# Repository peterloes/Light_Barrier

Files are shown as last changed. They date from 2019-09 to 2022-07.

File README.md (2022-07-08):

# Light barriers

A standalone platform for animal observation and manipulation.

This program is a software module for the hardware platform
"Light_Barrier_2015_3" developed for two pairs of lightbarriers.

Wide Input Voltage Range: 3.3V to 60V

Example with receiver from Vishay: TSSP58038 and LED Vishay: VSLB3940

Always low level triggered for wire monitoring(breakage).

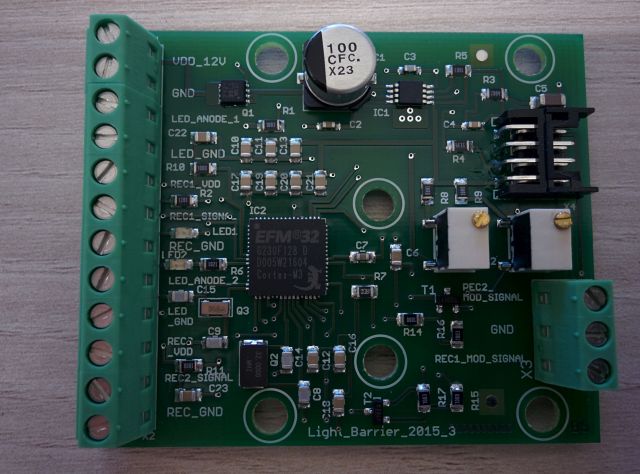
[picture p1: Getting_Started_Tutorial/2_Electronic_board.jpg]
My image


Two high level signal: 204µA@3,3V  -- Two low  level signal: 1.49mA@3,3V

Two high level signal: 195µA@5V    -- Two low  level signal: 1.49mA@5V

Two high level signal: 195µA@13,2V -- Two low  level signal: 1.47mA@13,2V

Parameter distance 3,3 Meter: 4mA@12V average

My image

Prototype: Bat counter 

The distance from light barrier 1 is 15cm and from light barrier 2 is 13cm.

https://github.com/peterloes/Light_Barrier/blob/master/Getting_Started_Tutorial/1_poster_overview_LightBarrier_Counter.pdf

Prototype: Long range RFID- reader for shore birds

https://github.com/peterloes/Light_Barrier/blob/master/Getting_Started_Tutorial/1_poster_overview_MOMO_LB_LR.pdf

Mainboard:

https://github.com/peterloes/MOMO

https://github.com/peterloes/RFID-MS

Manufacture:

https://github.com/peterloes/Light_Barrier/blob/master/Getting_Started_Tutorial/3_Supplier.txt

EXTENSION:

https://github.com/peterloes/SmartAnimalTraps

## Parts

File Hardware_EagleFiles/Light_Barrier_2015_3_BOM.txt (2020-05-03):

Partlist exported at 8/3/2016 8:29:31 AM

Part  Value                Device                  Package                Description                                                    
C1    100uF/16V            CPOL-EUE                PANASONIC_E            POLARIZED CAPACITOR, European symbol                           
C2    1uF                  C-EUC0603               C0603                  CAPACITOR, European symbol                                     
C3    1nF                  C-EUC0603               C0603                  CAPACITOR, European symbol                                     
C4    10nF                 C-EUC0603               C0603                  CAPACITOR, European symbol                                     
C5    10uF                 C-EUC1206               C1206                  CAPACITOR, European symbol                                     
C6    100n                 C_SMD0805               0805                                                                                  
C7    1u                   C_SMD0805               0805                                                                                  
C8    12p                  C_SMD0805               0805                                                                                  
C9    18p                  C_SMD0805               0805                                                                                  
C10   100n                 C_SMD0805               0805                                                                                  
C11   100n                 C_SMD0805               0805                                                                                  
C12   100n                 C_SMD0805               0805                                                                                  
C13   100n                 C_SMD0805               0805                                                                                  
C14   12p                  C_SMD0805               0805                                                                                  
C15   18p                  C_SMD0805               0805                                                                                  
C16   100n                 C_SMD0805               0805                                                                                  
C17   100n                 C_SMD0805               0805                                                                                  
C18   100n                 C_SMD0805               0805                                                                                  
C19   100n                 C_SMD0805               0805                                                                                  
C20   100n                 C_SMD0805               0805                                                                                  
C21   100n                 C_SMD0805               0805                                                                                  
C22   100n                 C-EUC0805               C0805                  CAPACITOR, European symbol                                     
C23   100n                 C-EUC0805               C0805                  CAPACITOR, European symbol                                     
IC1   TPS7A1601DGNT        TPS7A16                 DGN_S-PDSO-G8-EXP                                                                     
IC2   EFM32G230F128        EFM32G230F128           QFN64                  EFM32G230F128 Gecko Microcontroller in 9mm x 9mm QFN64 package 
LED1  SML-211UT            LEDCHIPLED_0805         CHIPLED_0805           LED                                                            
LED2  SML-211UT            LEDCHIPLED_0805         CHIPLED_0805           LED                                                            
PASS1 ROUND_1MM1.5         ROUND_1MM1.5            ROUND2_1.5MM                                                                          
PASS2 ROUND_1MM1.5         ROUND_1MM1.5            ROUND2_1.5MM                                                                          
Q1    SI7121DN             TRANSISTOR-FET_SI7113DN TRANSISTOR-FET_1212-8S                                                                
Q2    NX5032GA/32MHz/8pF   CRYSTAL2P5.0X3.2        CRYSTAL2P5.0X3.2       Quarz Crystal                                                  
Q3    CM7V, 32768Hz/12.5pF CRYSTAL2P               CRYSTAL2P3.2X1.5       Quarz Crystal                                                  
R1    100k                 R-EU_R0805              R0805                  RESISTOR, European symbol                                      
R2    1K2                  R-EU_R0805              R0805                  RESISTOR, European symbol                                      
R3    2M                   R-EU_R0805              R0805                  RESISTOR, European symbol                                      
R4    1M13                 R-EU_R0805              R0805                  RESISTOR, European symbol                                      
R5    100K                 R-EU_R0805              R0805                  RESISTOR, European symbol                                      
R6    1K2                  R-EU_R0805              R0805                  RESISTOR, European symbol                                      
R7    1                    R-EU_R0805              R0805                  RESISTOR, European symbol                                      
R8    18                   R-EU_R0805              R0805                  RESISTOR, European symbol                                      
R9    18                   R-EU_R0805              R0805                  RESISTOR, European symbol                                      
R10   100                  R-EU_R0805              R0805                  RESISTOR, European symbol                                      
R11   100                  R-EU_R0805              R0805                  RESISTOR, European symbol                                      
R12   50k(TS63)            R-TRIMMTS63Y            RTRIMTS63Y             Trimm resistor                                                 
R13   50k(TS63)            R-TRIMMTS63Y            RTRIMTS63Y             Trimm resistor                                                 
R14   100                  R-EU_R0805              R0805                  RESISTOR, European symbol                                      
R15   100                  R-EU_R0805              R0805                  RESISTOR, European symbol                                      
R16   100K                 R-EU_R0805              R0805                  RESISTOR, European symbol                                      
R17   100K                 R-EU_R0805              R0805                  RESISTOR, European symbol                                      
T1    2N7002               ZETEX_NMOSSOT23         ZETEX_SOT-23           MOS FET                                                        
T2    2N7002               ZETEX_NMOSSOT23         ZETEX_SOT-23           MOS FET                                                        
X1    MKDS1/2-3,81         MKDS1/2-3,81            2POL381                MKDS 1/2-3,81 - Order No. 1727010 (RS-Online - 101-5384)       
X2    MKDS1/10-3,81        MKDS1/10-3,81           10POL381               MKDS 1/10-3,81 - Order No. 1727094                             
X3    MKDS1/3-3,81         MKDS1/3-3,81            3POL381                MKDS 1/3-3,81 - Order No. 1727023 (RS-Online - 101-5390)       
X4    DF11_8DP_2DS         DP11_8DP_2DS            DP11_8DP-2DS

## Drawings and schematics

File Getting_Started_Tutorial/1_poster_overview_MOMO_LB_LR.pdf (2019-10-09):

## Multifunctional Mainboard to Observe and Manipulate Organisms (MOMO) Light Barrier and Long Range Reader

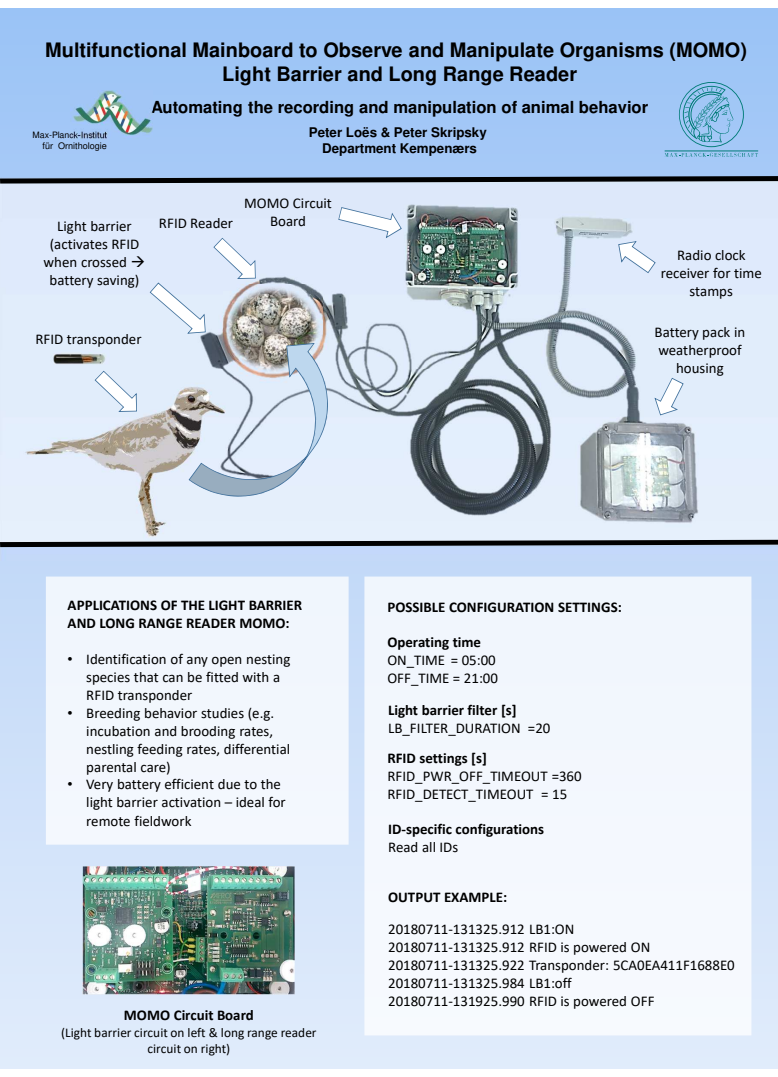
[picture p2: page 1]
APPLICATIONS OF THE LIGHT BARRIER; POSSIBLE CONFIGURATION SETTINGS:; RFID Reader; RFID transponder; Operating time ON_TIME = 05:00 OFF_TIME = 21:00; MOMO Circuit Board; Light barrier (activates RFID when crossed → battery saving); RFID settings [s] RFID_PWR_OFF_TIMEOUT =360 RFID_DETECT_TIMEOUT = 15; OUTPUT EXAMPLE:

Automating the recording and manipulation of animal behavior

Peter Loës & Peter Skripsky
Department Kempenærs

Max-Planck-Institut
für Ornithologie

Radio clock
receiver for time
stamps

Battery pack in
weatherproof
housing

AND LONG RANGE READER MOMO:

• Identification of any open nesting
species that can be fitted with a
RFID transponder
• Breeding behavior studies (e.g.
incubation and brooding rates,
nestling feeding rates, differential
parental care)
• Very battery efficient due to the
light barrier activation – ideal for
remote fieldwork

Light barrier filter [s]
LB_FILTER_DURATION =20

ID-specific configurations
Read all IDs

20180711-131325.912 RFID is powered ON
20180711-131325.922 Transponder: 5CA0EA411F1688E0
20180711-131325.984 LB1:off
20180711-131925.990 RFID is powered OFF

MOMO Circuit Board

(Light barrier circuit on left & long range reader

circuit on right)

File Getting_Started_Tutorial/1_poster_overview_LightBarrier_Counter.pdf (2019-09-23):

### Light Barrier Counter

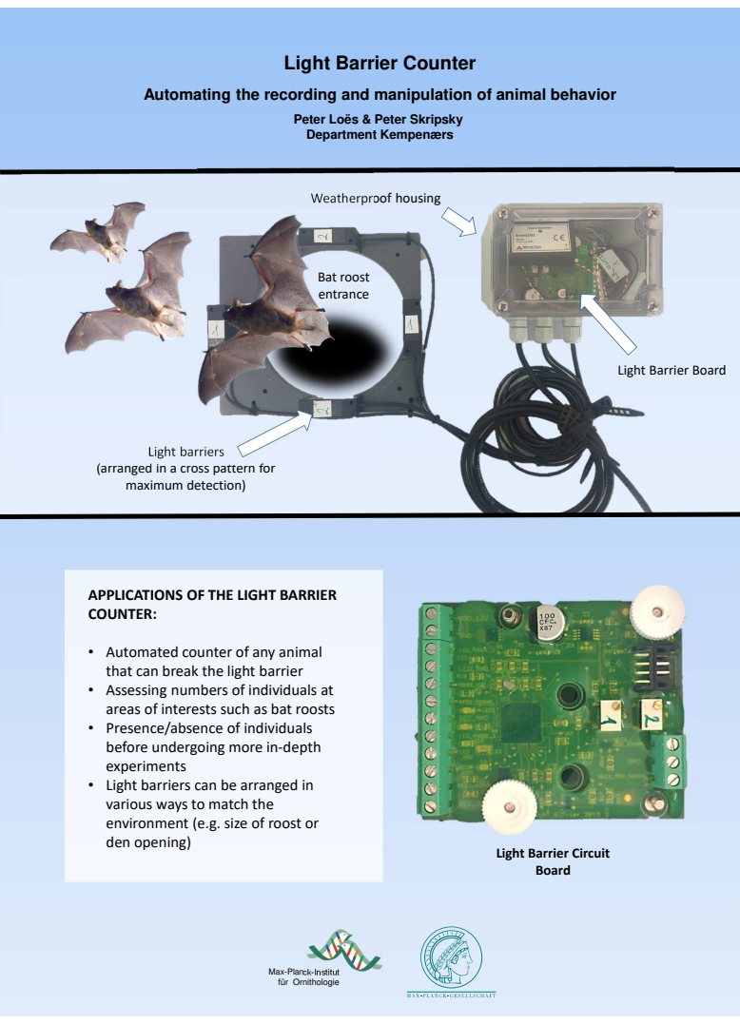
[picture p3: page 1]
Board; Weatherproof housing; Light barriers; Bat roost entrance

Automating the recording and manipulation of animal behavior

Peter Loës & Peter Skripsky
Department Kempenærs

Light Barrier Board

(arranged in a cross pattern for
maximum detection)

APPLICATIONS OF THE LIGHT BARRIER
COUNTER:

• Automated counter of any animal
that can break the light barrier
• Assessing numbers of individuals at
areas of interests such as bat roosts
• Presence/absence of individuals
before undergoing more in-depth
experiments
• Light barriers can be arranged in
various ways to match the
environment (e.g. size of roost or
den opening)

Light Barrier Circuit

Max-Planck-Institut
für Ornithologie

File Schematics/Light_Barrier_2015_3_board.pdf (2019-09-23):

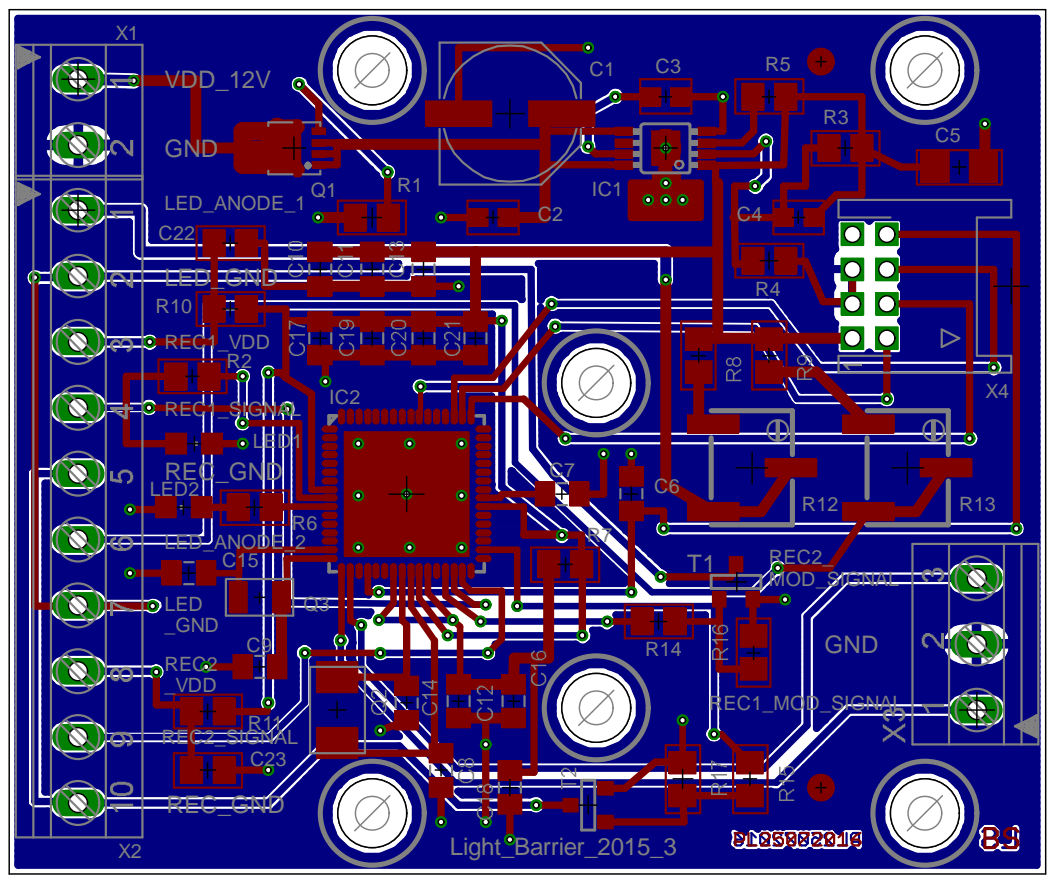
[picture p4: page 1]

GND

LED_ANODE_1
C22

LED1

R11
C23

REC2_SIGNAL

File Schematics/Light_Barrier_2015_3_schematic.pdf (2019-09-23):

# Power Input

# EFM32 Power Regulator

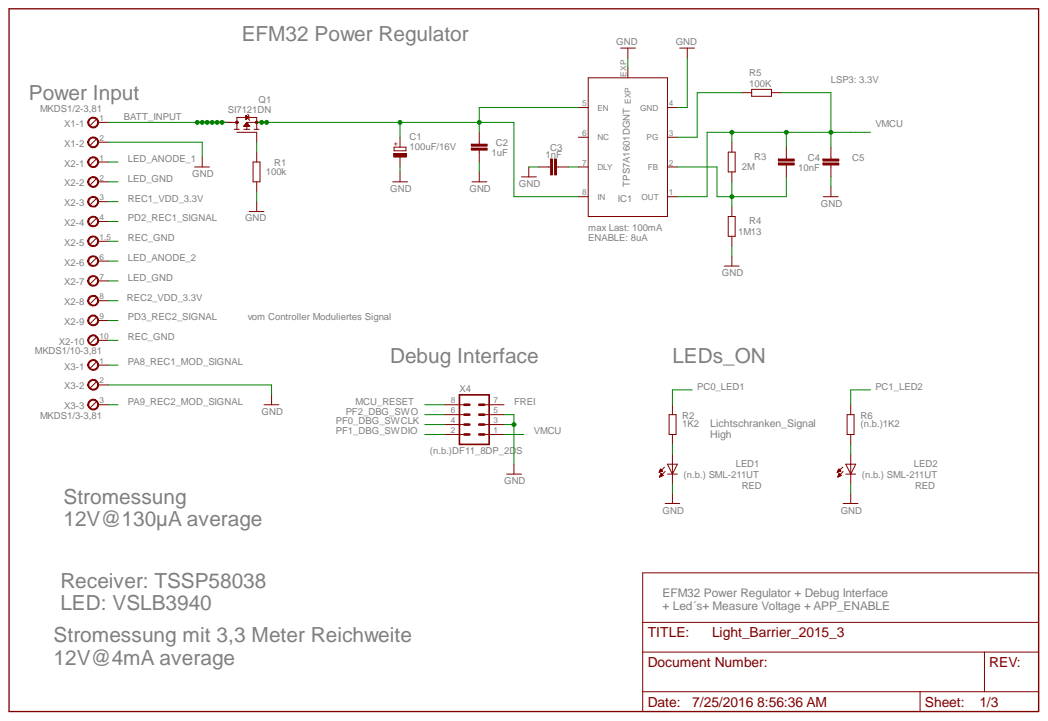
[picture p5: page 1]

vom Controller Moduliertes Signal

EFM32 Power Regulator + Debug Interface
+ Led´s+ Measure Voltage + APP_ENABLE
TITLE:

Document Number: | REV:

Date: 7/25/2016 8:56:36 AM | Sheet: 1/3

# EFM32 I/O + POWER

# CL f. 32KHz crystal = 22pF as in STK3600

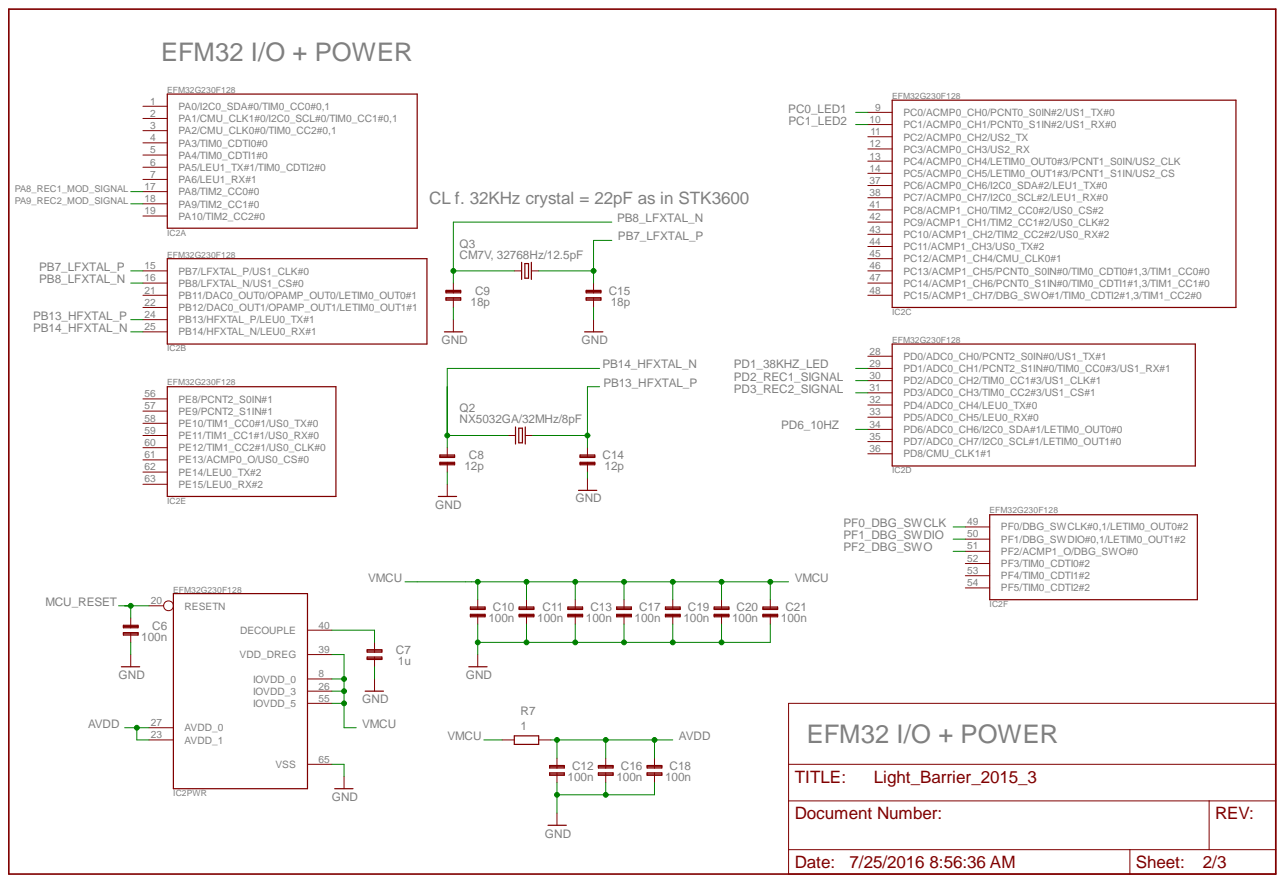
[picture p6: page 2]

Document Number: | REV:

Date: 7/25/2016 8:56:36 AM | Sheet: 2/3

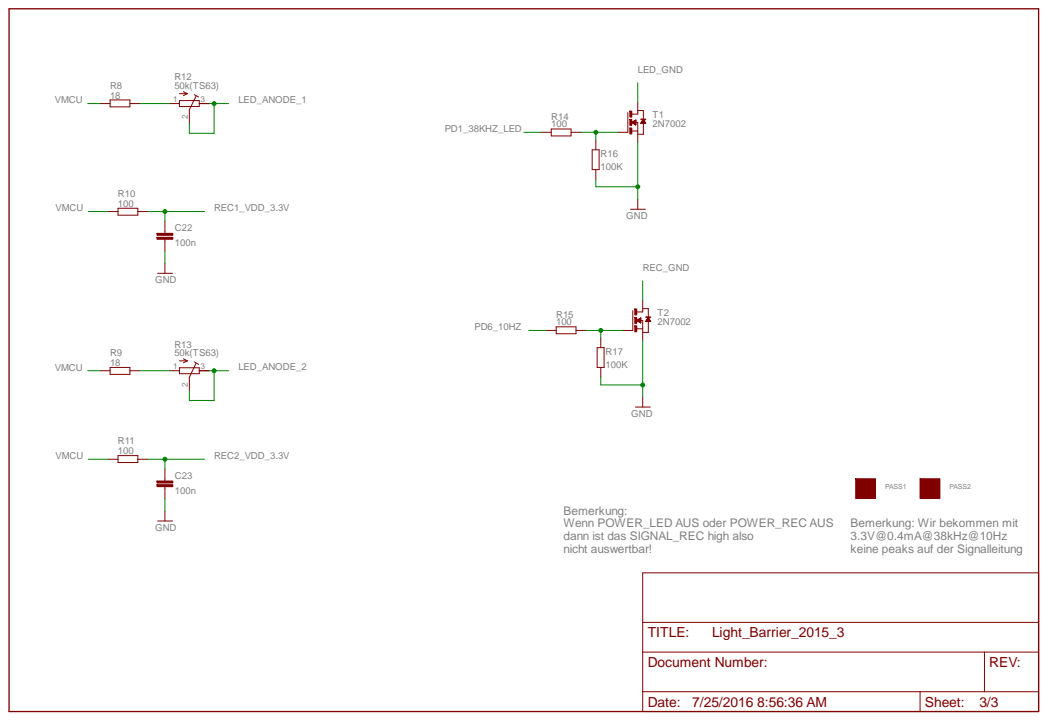
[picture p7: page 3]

Bemerkung:
Wenn POWER_LED AUS oder POWER_REC AUS
dann ist das SIGNAL_REC high also
nicht auswertbar!

Bemerkung: Wir bekommen mit
3.3V@0.4mA@38kHz@10Hz
keine peaks auf der Signalleitung

Document Number: | REV:

Date: 7/25/2016 8:56:36 AM | Sheet: 3/3

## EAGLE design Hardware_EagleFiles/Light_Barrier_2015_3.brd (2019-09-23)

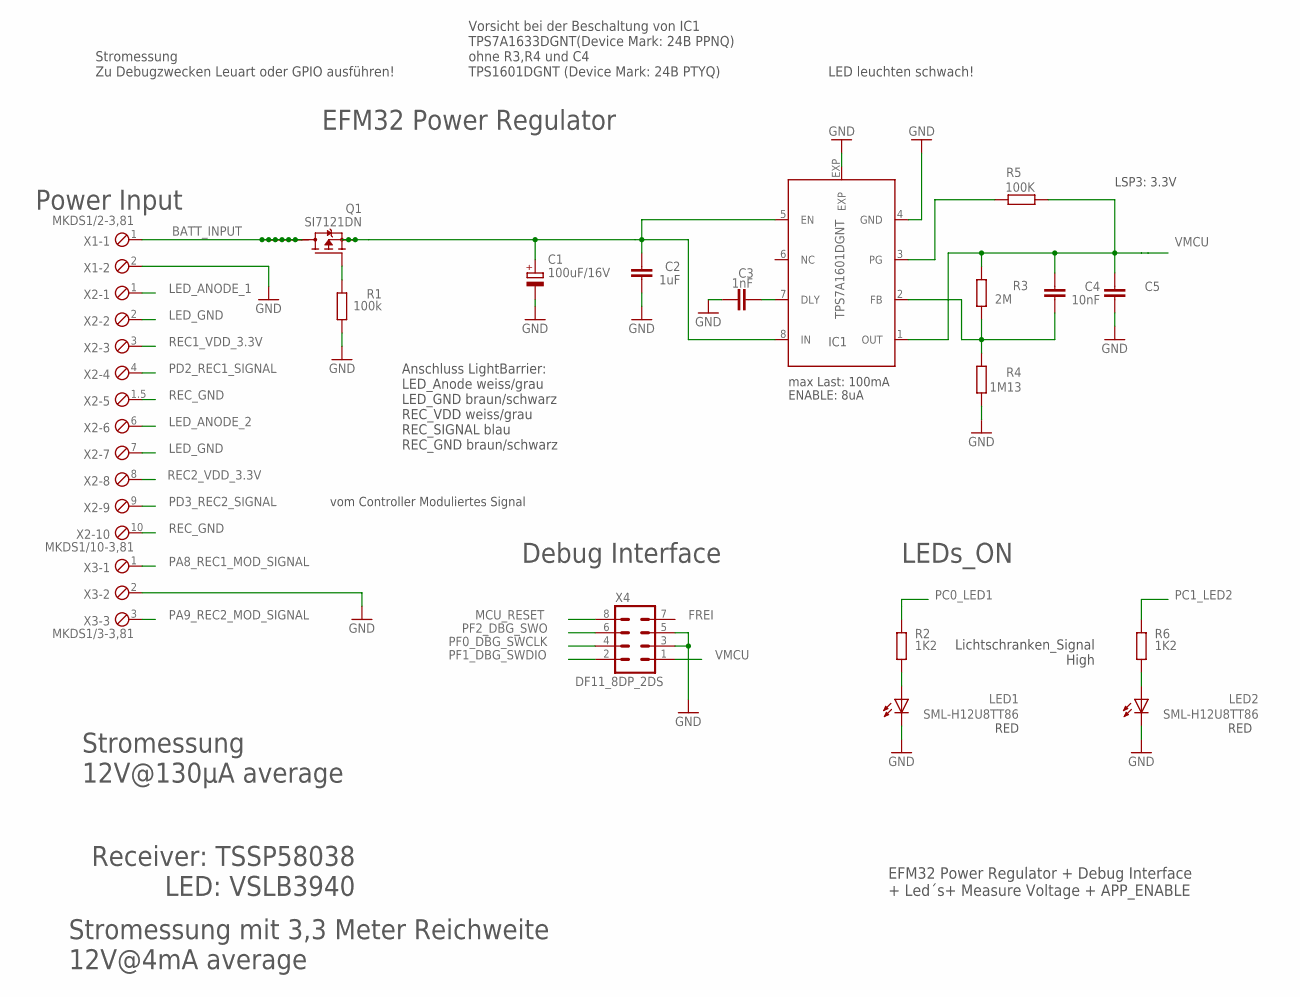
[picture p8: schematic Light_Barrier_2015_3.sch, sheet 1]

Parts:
C1: 100uF/16V; PANASONIC_E
C2: 1uF; C0603
C3: 1nF; C0603
C4: 10nF; C0603
C5: 10uF; C1206
IC1: TPS7A1601DGNT; DGN_S-PDSO-G8-EXP
LED1, LED2: SML-H12U8TT86; CHIPLED_0805
Q1: SI7121DN; TRANSISTOR-FET_1212-8S
R1: 100k; R0805
R2, R6: 1K2; R0805
R3: 2M; R0805
R4: 1M13; R0805
R5: 100K; R0805
X1: MKDS1/2-3,81; 2POL381
X2: MKDS1/10-3,81; 10POL381
X3: MKDS1/3-3,81; 3POL381
X4: DF11_8DP_2DS; DP11_8DP-2DS

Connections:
BATT_INPUT: Q1.5 (D), Q1.6 (D), Q1.7 (D), Q1.8 (D), Q1.9 (D), Q1.10 (D), Q1.11 (D), X1.1
GND: C1.-, C2.1, C3.1, C5.1, IC1.4 (GND), IC1.EXP, LED1.C, LED2.C, R1.1, R4.1, X1.2, X3.2, X4.3, X4.5; also elsewhere on the board
LED_ANODE_1: X2.1; also elsewhere on the board
LED_ANODE_2: X2.6; also elsewhere on the board
LED_GND: X2.2, X2.7; also elsewhere on the board
MCU_RESET: X4.8; also elsewhere on the board
unnamed: C4.1, IC1.2 (FB), R3.1, R4.2
unnamed: C3.2, IC1.7 (DLY)
unnamed: C1.+, C2.2, IC1.5 (EN), IC1.8 (IN), Q1.1 (S), Q1.2 (S), Q1.3 (S)
unnamed: IC1.3 (PG), R5.2
unnamed: Q1.4 (G), R1.2
unnamed: LED1.A, R2.2
unnamed: LED2.A, R6.2
PA8_REC1_MOD_SIGNAL: X3.1; also elsewhere on the board
PA9_REC2_MOD_SIGNAL: X3.3; also elsewhere on the board
PC0_LED1: R2.1; also elsewhere on the board
PC1_LED2: R6.1; also elsewhere on the board
PD2_REC1_SIGNAL: X2.4; also elsewhere on the board
PD3_REC2_SIGNAL: X2.9; also elsewhere on the board
PF0_DBG_SWCLK: X4.4; also elsewhere on the board
PF1_DBG_SWDIO: X4.2; also elsewhere on the board
PF2_DBG_SWO: X4.6; also elsewhere on the board
REC1_VDD_3.3V: X2.3; also elsewhere on the board
REC2_VDD_3.3V: X2.8; also elsewhere on the board
REC_GND: X2.1.5, X2.10; also elsewhere on the board
VMCU: C4.2, C5.2, IC1.1 (OUT), R3.2, R5.1, X4.1; also elsewhere on the board

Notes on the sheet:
EFM32 Power Regulator + Debug Interface + Led´s+ Measure Voltage + APP_ENABLE
ENABLE: 8uA
Power Input
max Last: 100mA
LSP3: 3.3V
EFM32 Power Regulator
Debug Interface
LEDs_ON
FREI
RED
Receiver: TSSP58038 LED: VSLB3940
Lichtschranken_Signal High
vom Controller Moduliertes Signal
Stromessung 12V@130µA average
Stromessung mit 3,3 Meter Reichweite 12V@4mA average
Stromessung Zu Debugzwecken Leuart oder GPIO ausführen!
Vorsicht bei der Beschaltung von IC1 TPS7A1633DGNT(Device Mark: 24B PPNQ) ohne R3,R4 und C4 TPS1601DGNT (Device Mark: 24B PTYQ)
LED leuchten schwach!
Anschluss LightBarrier: LED_Anode weiss/grau LED_GND braun/schwarz REC_VDD weiss/grau REC_SIGNAL blau REC_GND braun/schwarz

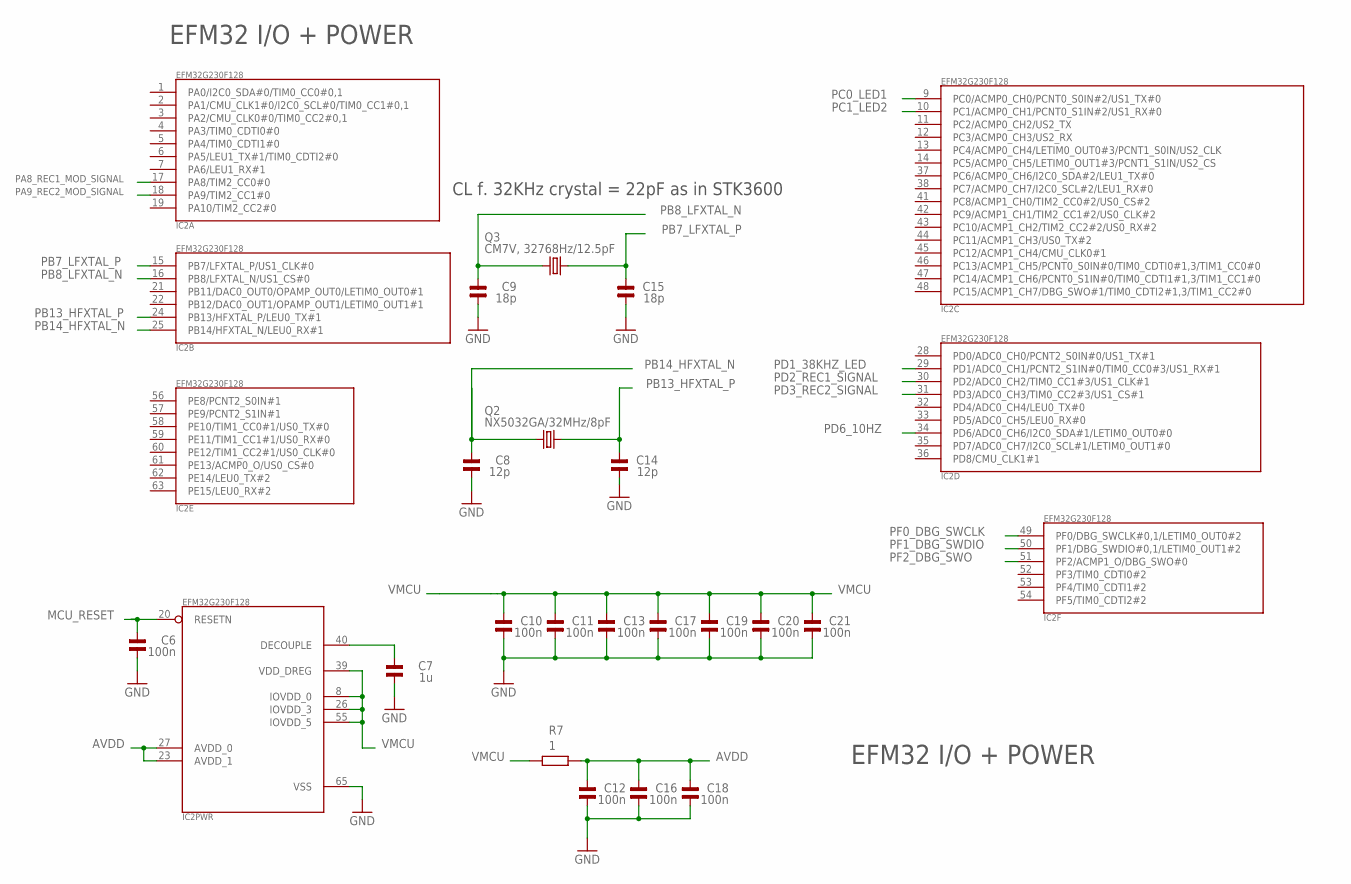
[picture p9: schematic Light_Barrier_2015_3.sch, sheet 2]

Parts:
C6, C10, C11, C12, C13, C16, C17, C18, C19, C20, C21: 100n; 0805
C7: 1u; 0805
C8, C14: 12p; 0805
C9, C15: 18p; 0805
IC2: EFM32G230F128; QFN64
Q2: NX5032GA/32MHz/8pF; CRYSTAL2P5.0X3.2
Q3: CM7V, 32768Hz/12.5pF; CRYSTAL2P3.2X1.5
R7: 1; R0805

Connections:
AVDD: C12.2, C16.2, C18.2, IC2.23 (AVDD_1), IC2.27 (AVDD_0), R7.2
GND: C6.1, C7.1, C8.1, C9.1, C10.1, C11.1, C12.1, C13.1, C14.1, C15.1, C16.1, C17.1, C18.1, C19.1, C20.1, C21.1, IC2.65 (VSS); also elsewhere on the board
MCU_RESET: C6.2, IC2.20 (RESETN); also elsewhere on the board
unnamed: C7.2, IC2.40 (DECOUPLE)
PA8_REC1_MOD_SIGNAL: IC2.17 (PA8/TIM2_CC0#0); also elsewhere on the board
PA9_REC2_MOD_SIGNAL: IC2.18 (PA9/TIM2_CC1#0); also elsewhere on the board
PB7_LFXTAL_P: C15.2, IC2.15 (PB7/LFXTAL_P/US1_CLK#0), Q3.2
PB8_LFXTAL_N: C9.2, IC2.16 (PB8/LFXTAL_N/US1_CS#0), Q3.1
PB13_HFXTAL_P: C14.2, IC2.24 (PB13/HFXTAL_P/LEU0_TX#1), Q2.2
PB14_HFXTAL_N: C8.2, IC2.25 (PB14/HFXTAL_N/LEU0_RX#1), Q2.1
PC0_LED1: IC2.9 (PC0/ACMP0_CH0/PCNT0_S0IN#2/US1_TX#0); also elsewhere on the board
PC1_LED2: IC2.10 (PC1/ACMP0_CH1/PCNT0_S1IN#2/US1_RX#0); also elsewhere on the board
PD1_38KHZ_LED: IC2.29 (PD1/ADC0_CH1/PCNT2_S1IN#0/TIM0_CC0#3/US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); also elsewhere on the board
PD2_REC1_SIGNAL: IC2.30 (PD2/ADC0_CH2/TIM0_CC1#3/US1_CLK#1); also elsewhere on the board
PD3_REC2_SIGNAL: IC2.31 (PD3/ADC0_CH3/TIM0_CC2#3/US1_CS#1); also elsewhere on the board
PD6_10HZ: IC2.34 (PD6/ADC0_CH6/I2C0_SDA#1/LETIM0_OUT0#0); also elsewhere on the board
PF0_DBG_SWCLK: IC2.49 (PF0/DBG_SWCLK#0,1/LETIM0_OUT0#2); also elsewhere on the board
PF1_DBG_SWDIO: IC2.50 (PF1/DBG_SWDIO#0,1/LETIM0_OUT1#2); also elsewhere on the board
PF2_DBG_SWO: IC2.51 (PF2/ACMP1_O/DBG_SWO#0); also elsewhere on the board
VMCU: C10.2, C11.2, C13.2, C17.2, C19.2, C20.2, C21.2, IC2.8 (IOVDD_0), IC2.26 (IOVDD_3), IC2.39 (VDD_DREG), IC2.55 (IOVDD_5), R7.1; also elsewhere on the board

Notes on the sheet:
EFM32 I/O + POWER
CL f. 32KHz crystal = 22pF as in STK3600

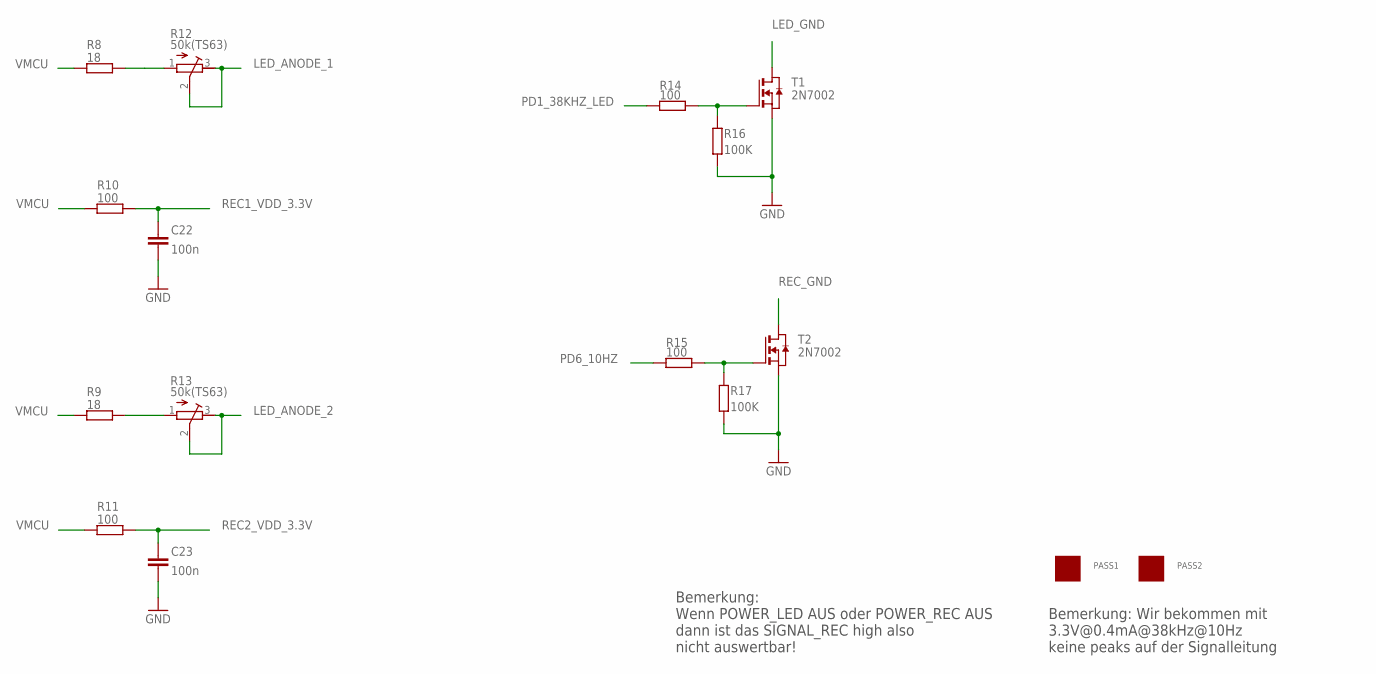
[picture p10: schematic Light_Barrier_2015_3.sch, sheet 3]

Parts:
C22, C23: 100n; C0805
PASS1, PASS2: ROUND_1MM1.5; ROUND2_1.5MM
R8, R9: 18; R0805
R10, R11, R14, R15: 100; R0805
R12, R13: 50k(TS63); RTRIMTS63Y
R16, R17: 100K; R0805
T1, T2: 2N7002; ZETEX_SOT-23

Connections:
GND: C22.2, C23.2, R16.1, R17.1, T1.2 (S), T2.2 (S); also elsewhere on the board
LED_ANODE_1: R12.2 (S), R12.3 (E); also elsewhere on the board
LED_ANODE_2: R13.2 (S), R13.3 (E); also elsewhere on the board
LED_GND: T1.1 (D); also elsewhere on the board
unnamed: R9.2, R13.1 (A)
unnamed: R8.2, R12.1 (A)
unnamed: R14.1, R16.2, T1.3 (G)
unnamed: R15.1, R17.2, T2.3 (G)
PD1_38KHZ_LED: R14.2; also elsewhere on the board
PD6_10HZ: R15.2; also elsewhere on the board
REC1_VDD_3.3V: C22.1, R10.2; also elsewhere on the board
REC2_VDD_3.3V: C23.1, R11.2; also elsewhere on the board
REC_GND: T2.1 (D); also elsewhere on the board
VMCU: R8.1, R9.1, R10.1, R11.1; also elsewhere on the board

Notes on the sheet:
Bemerkung: Wir bekommen mit 3.3V@0.4mA@38kHz@10Hz keine peaks auf der Signalleitung
Bemerkung: Wenn POWER_LED AUS oder POWER_REC AUS dann ist das SIGNAL_REC high also nicht auswertbar!

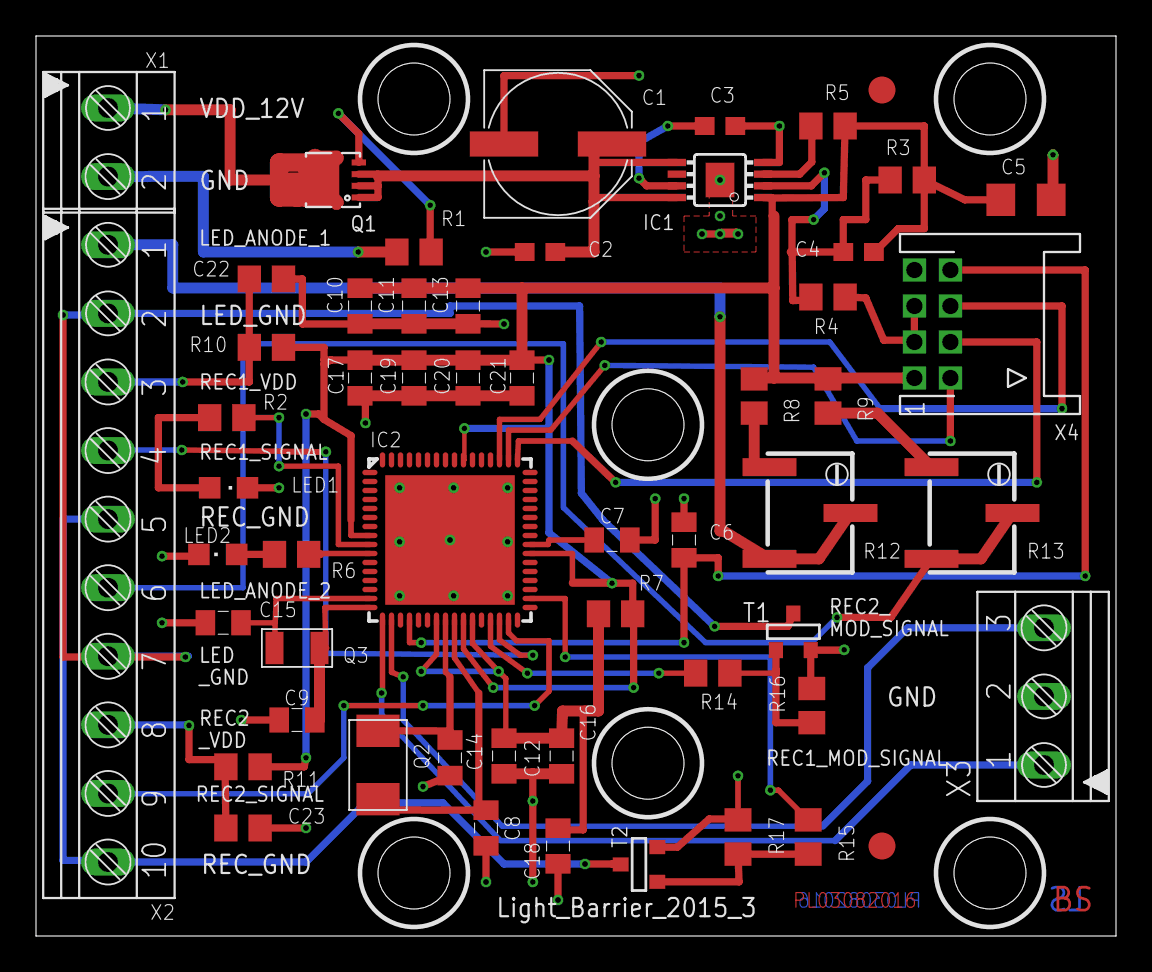
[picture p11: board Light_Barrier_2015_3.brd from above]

Board: 4 copper layers, 60.0 x 50.0 mm, 55 parts (0 on the bottom side), 38 nets.

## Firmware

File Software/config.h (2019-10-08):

/***************************************************************************//**
 * @file
 * @brief	Project configuration file
 * @author	Ralf Gerhauser
 * @version	2016-06-22
 *
 * This file allows to set miscellaneous configuration parameters.  It must be
 * included by all modules.
 *
 ****************************************************************************//*
Revision History:
2016-06-22,rage	Derived from project "SNB_Heaven".
*/

#ifndef __INC_config_h
#define __INC_config_h

/*=============================== Header Files ===============================*/

#include <stdio.h>
#include <stdbool.h>
#include "em_device.h"

/*=============================== Definitions ================================*/

/*
 * Basic defines - should all be moved to Generic.h
 */
    /* terminators for lists and strings */

#define	EOL		NULL		/* EndOfList		*/
#define EOS		'\0'		/* EndOfString		*/
#define	NONE		(-1)

    /* macro to calculate the number of elements of an array */
#define ELEM_CNT(array)  (sizeof (array) / sizeof ((array)[0]))

/*
 * Port numbers - used to select a dedicated configuration for IR_LED_PORT_NUM
 */
#define GPIO_PORT_A	0
#define GPIO_PORT_B	1
#define GPIO_PORT_C	2
#define GPIO_PORT_D	3
#define GPIO_PORT_E	4

/*!
 * @brief MPU Clock Configuration.
 *
 * Set to 0 to use the internal RC oscillator, if 1 the external 32MHz XTAL
 * is used.
 */
#define USE_EXT_32MHZ_CLOCK	0

/*
 * Configuration for module "LightBarrier2"
 */
    /*!@brief LETIMER frequency in [Hz]. */
#define LETIMER_COUNTS_PER_SEC	32768

    /*!@brief Define PWM frequency for IR LED in [Hz] */
#define LB2_PWM_FREQ		37835	// nearly 38kHz


/*================================== Macros ==================================*/

    /*! Macro to address a single bit in the I/O range (peripheral range) in
     *  an atomic manner.
     * @param address   I/O register address.
     * @param bitNum    Bit number within this register.
     */
#define IO_BIT_ADDR(address, bitNum)					\
	((__IO uint32_t *) (BITBAND_PER_BASE				\
			+ (((uint32_t)(address)) - PER_MEM_BASE) * 32	\
			+ (bitNum) * 4))

    /*! Shortcut to directly access an I/O-bit. */
#define IO_Bit(regName, bitNum)	*IO_BIT_ADDR(&regName, bitNum)

    /*! Macro to address a single bit in an SRAM variable in an atomic manner.
     * @param address   Address of the variable in SRAM.
     * @param bitNum    Bit number within this variable.
     */
#define SRAM_BIT_ADDR(address, bitNum)					\
	((__IO uint32_t *) (BITBAND_RAM_BASE				\
			+ (((uint32_t)(address)) - RAM_MEM_BASE) * 32	\
			+ (bitNum) * 4))

    /*! Shortcut to directly access a bit in a variable. */
#define Bit(varName, bitNum)	*SRAM_BIT_ADDR(&varName, bitNum)

/*=========================== Typedefs and Structs ===========================*/

/*!@brief Enumeration of the EM1 Modules
 *
 * This is the list of Software Modules that require EM1 to work, i.e. they
 * will not work in EM2 because clocks, etc. would be disabled.  These enums
 * are used to set/clear the appropriate bit in the @ref g_EM1_ModuleMask.
 */
typedef enum
{
    EM1_MOD_IR_LED_TIMER,	//!<  0: 38kHz timer requires EM1 for its clock
    END_EM1_MODULES
} EM1_MODULES;

/*======================== External Data and Routines ========================*/

extern volatile bool	 g_flgIRQ;		// Flag: Interrupt occurred
extern volatile uint16_t g_EM1_ModuleMask;	// Modules that require EM1


#endif /* __INC_config_h */

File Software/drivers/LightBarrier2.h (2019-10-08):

/***************************************************************************//**
 * @file
 * @brief	Header file of module LightBarrier2.c
 * @author	Ralf Gerhauser
 * @version	2016-11-18
 ****************************************************************************//*
Revision History:
2016-11-18,rage	Changes for hardware platform Light_Barrier_2015_3:
		- Support 2nd light barrier on PD3.
		- The signal to enable the IR receivers is now high-active.
2016-07-14,rage	Changed GPIO_PORT_X defines to gpioPortX to prevent IAR compiler
		warning, except IR_LED_PORT_NUM which uses GPIO_PORT_X to select
		a dedicated pin, timer, and CC channel configuration.
2016-06-22,rage	Initial version.
*/

#ifndef __INC_LightBarrier2_h
#define __INC_LightBarrier2_h

/*=============================== Header Files ===============================*/

#include "em_device.h"
#include "em_gpio.h"
#include "config.h"		// include project configuration parameters

/*=============================== Definitions ================================*/

/*!@brief Power-on duration in [ms] for IR LED and receiver circuit.
 * Default is 6ms.
 */
#ifndef LB2_POWER_ON
  #define LB2_POWER_ON		 6
#endif

/*!@brief Power-off duration in [ms] for IR LED and receiver circuit.
 * Default is 94ms to perform a 100ms rate (power-on time is 6ms).
 */
#ifndef LB2_POWER_OFF
  #define LB2_POWER_OFF		94
#endif

/*!@brief PWM frequency for the Infrared LED in [Hz]
 * Default is 38kHz.
 */
#ifndef LB2_PWM_FREQ
  #define LB2_PWM_FREQ		38000
#endif


/*!@brief Port and pin selection for the GPIO that enables the Infrared Receiver
 * circuits.  These defines can also be set in the project configuration file
 * "config.h".  Default is PD6.  This pin is high-active.
 */
#ifndef IR_RX_ENA_PORT
  #define IR_RX_ENA_PORT	gpioPortD
#endif
#ifndef IR_RX_ENA_PIN
  #define IR_RX_ENA_PIN		6
#endif


/*!@brief Port and pin selection for the input signal from Infrared Receiver #1
 * circuit.  These defines can also be set in the project configuration file
 * "config.h".  Default is PD2.
 */
#ifndef IR1_RX_INP_PORT
  #define IR1_RX_INP_PORT	gpioPortD
#endif
#ifndef IR1_RX_INP_PIN
  #define IR1_RX_INP_PIN	2
#endif


/*!@brief Port and pin selection for the input signal from Infrared Receiver #2
 * circuit.  These defines can also be set in the project configuration file
 * "config.h".  Default is PD3.
 */
#ifndef IR2_RX_INP_PORT
  #define IR2_RX_INP_PORT	gpioPortD
#endif
#ifndef IR2_RX_INP_PIN
  #define IR2_RX_INP_PIN	3
#endif


/*!@brief Port and pin selection for the Infrared LEDs which are hardware
 * controlled by one of the timers. These defines can also be set in the
 * project configuration file "config.h".  Default is PD1.
 * The following GPIO pins are valid: PA0, PA1, PA2, PA8, PA9, PA10, PC8, PC9,
 * PC10, PC13, PC14, PC15, PD1, PD2, and PD3.
 *
 * Use defines GPIO_PORT_A to E, do *not* use gpioPortA to E.
 */
#ifndef IR_LED_PORT_NUM
  #define IR_LED_PORT_NUM	GPIO_PORT_D
#endif
#ifndef IR_LED_PIN
  #define IR_LED_PIN		1
#endif

/* automatically selects the right timer, CC channel, and routing */
#if IR_LED_PORT_NUM == GPIO_PORT_A  &&  IR_LED_PIN >= 0  &&  IR_LED_PIN <= 2
  #define IR_LED_PORT		gpioPortA
  #define IR_LED_TIMER_NUM	0
  #define IR_LED_CC_LOC		TIMER_ROUTE_LOCATION_LOC0
  #define IR_LED_CC_NUM		(IR_LED_PIN)
#elif IR_LED_PORT_NUM == GPIO_PORT_A  &&  IR_LED_PIN >= 8  &&  IR_LED_PIN <= 10
  #define IR_LED_PORT		gpioPortA
  #define IR_LED_TIMER_NUM	2
  #define IR_LED_CC_LOC		TIMER_ROUTE_LOCATION_LOC0
  #define IR_LED_CC_NUM		(IR_LED_PIN - 8)
#elif IR_LED_PORT_NUM == GPIO_PORT_C  &&  IR_LED_PIN >= 8  &&  IR_LED_PIN <= 10
  #define IR_LED_PORT		gpioPortC
  #define IR_LED_TIMER_NUM	2
  #define IR_LED_CC_LOC		TIMER_ROUTE_LOCATION_LOC2
  #define IR_LED_CC_NUM		(IR_LED_PIN - 8)
#elif IR_LED_PORT_NUM == GPIO_PORT_C  &&  IR_LED_PIN >= 13  &&  IR_LED_PIN <= 15
  #define IR_LED_PORT		gpioPortC
  #define IR_LED_TIMER_NUM	1
  #define IR_LED_CC_LOC		TIMER_ROUTE_LOCATION_LOC0
  #define IR_LED_CC_NUM		(IR_LED_PIN - 13)
#elif IR_LED_PORT_NUM == GPIO_PORT_D  &&  IR_LED_PIN >= 1  &&  IR_LED_PIN <= 3
  #define IR_LED_PORT		gpioPortD
  #define IR_LED_TIMER_NUM	0
  #define IR_LED_CC_LOC		TIMER_ROUTE_LOCATION_LOC3
  #define IR_LED_CC_NUM		(IR_LED_PIN - 1)
#elif IR_LED_PORT_NUM == GPIO_PORT_E  &&  IR_LED_PIN >= 10  &&  IR_LED_PIN <= 12
  #define IR_LED_PORT		gpioPortE
  #define IR_LED_TIMER_NUM	1
  #define IR_LED_CC_LOC		TIMER_ROUTE_LOCATION_LOC1
  #define IR_LED_CC_NUM		(IR_LED_PIN - 10)
#else
  #error "Invalid selection for IR_LED_PORT and/or IR_LED_PIN"
#endif

/* resulting defines from the configuration above */
#if IR_LED_TIMER_NUM == 0
  #define IR_LED_TIMER		TIMER0
  #define IR_LED_CMU_CLOCK	cmuClock_TIMER0
#elif IR_LED_TIMER_NUM == 1
  #define IR_LED_TIMER		TIMER1
  #define IR_LED_CMU_CLOCK	cmuClock_TIMER1
#elif IR_LED_TIMER_NUM == 2
  #define IR_LED_TIMER		TIMER2
  #define IR_LED_CMU_CLOCK	cmuClock_TIMER2
#endif

#if IR_LED_CC_NUM == 0
  #define IR_LED_CC_PEN		TIMER_ROUTE_CC0PEN
#elif IR_LED_CC_NUM == 1
  #define IR_LED_CC_PEN		TIMER_ROUTE_CC1PEN
#elif IR_LED_CC_NUM == 2
  #define IR_LED_CC_PEN		TIMER_ROUTE_CC2PEN
#endif

/* check if required defines are set */
#ifndef IR_LED_TIMER
  #error "Define IR_LED_TIMER could not be set, check IR_LED_PORT, IR_LED_PIN"
#endif
#ifndef IR_LED_CC_PEN
  #error "Define IR_LED_CC_PEN could not be set, check IR_LED_PORT, IR_LED_PIN"
#endif

/*================================ Global Data ===============================*/

extern volatile uint32_t  g_LB_ActiveMask;

/*================================ Prototypes ================================*/

/* Initialize Light Barrier hardware */
void	LB2_Init (void);

/*
 * External light Barrier handler, called from interrupt service routine.
 * This call-out routine must be provided by another module.
 */
void	LP2_SignalState (int num, bool state);


#endif /* __INC_LightBarrier2_h */

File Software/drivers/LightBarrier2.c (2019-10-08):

/***************************************************************************//**
 * @file
 * @brief	Logic for discrete Light Barrier - Type 2
 * @author	Peter Loës
 * @version	2016-11-18
 *
 * This module provides the logic for the light barriers of type 2.  With this
 * implementation, the PWM signal for the IR LEDs is generated by an EFM32
 * timer, and LETIMER0 is used to enable the circuitry just for an adjustable
 * amount of time to save power.
 *
 * An interrupt service routine checks the current state of the light barrier
 * beams and calls an externally provided function to introduce any signal
 * changes.  Prototype of this function:
 *
 * @code
 * void LP2_SignalState (int num, bool state)
 * @endcode
 *
 * Parameter <i>num</i> contains the index of the two light barriers: 0 for
 * LB1, and 1 for LB2.
 *
 * Parts of the code are based on the example code of AN0026 "LETIMER demo
 * application, PWM and pulse output" from Energy Micro AS.
 *
 ***************************************************************************//**
 *
 * Parts are Copyright 2013 Energy Micro AS, http://www.energymicro.com
 *
 *******************************************************************************
 *
 * Permission is granted to anyone to use this software for any purpose,
 * including commercial applications, and to alter it and redistribute it
 * freely, subject to the following restrictions:
 *
 * 1. The origin of this software must not be misrepresented; you must not
 *    claim that you wrote the original software.
 * 2. Altered source versions must be plainly marked as such, and must not be
 *    misrepresented as being the original software.
 * 3. This notice may not be removed or altered from any source distribution.
 * 4. The source and compiled code may only be used on Energy Micro "EFM32"
 *    microcontrollers and "EFR4" radios.
 *
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
 * Energy Micro AS will not be liable for any consequential, incidental, or
 * special damages, or any other relief, or for any claim by any third party,
 * arising from your use of this Software.
 *
 ****************************************************************************//*
Revision History:
2016-11-18,rage	Changes for hardware platform Light_Barrier_2015_3:
		- Support 2nd light barrier on PD3.
		- The signal to enable the IR receivers is now high-active.
2016-06-22,rage	Extracted code from main to build this module.
2016-03-23,Loës	Initial version.
*/

/*=============================== Header Files ===============================*/

#include "em_cmu.h"
#include "em_gpio.h"
#include "em_letimer.h"
#include "em_timer.h"

#include "LightBarrier2.h"

/*=============================== Definitions ================================*/

#define TIMER_TOP_VALUE (CMU_ClockFreqGet(cmuClock_HFPER) / LB2_PWM_FREQ)
#define POWER_ON_COMP_VALUE (LETIMER_COUNTS_PER_SEC * LB2_POWER_ON / 1000)
#define POWER_OFF_COMP_VALUE (LETIMER_COUNTS_PER_SEC * LB2_POWER_OFF / 1000)

/*================================ Local Data ================================*/

/* previous state of the light barriers */
static int l_prevLB1_State;
static int l_prevLB2_State;

/*=========================== Forward Declarations ===========================*/

static void PWM_TimerSetup(void);
static void LETIMER0_setup(void);


/***************************************************************************//**
 *
 * @brief	Initialize the light barrier hardware of type 2
 *
 * This routine initializes the board-specific hardware for the light
 * barrier of type 2.  With this implementation of a light barrier, the PWM
 * signal for the IR LED ist generated by an EFM32 timer, and LETIMER0 is
 * used to enable the circuitry just for a adjustable amount of time to save
 * power.
 *
 ******************************************************************************/
void	LB2_Init (void)
{
    /* Be sure to enable clock to GPIO (should already be done) */
    CMU_ClockEnable (cmuClock_GPIO, true);

    /* Initialize the GPIO for the input signal from the IR receivers */
    GPIO_PinModeSet(IR1_RX_INP_PORT, IR1_RX_INP_PIN, gpioModeInput, 0);
    GPIO_PinModeSet(IR2_RX_INP_PORT, IR2_RX_INP_PIN, gpioModeInput, 0);

    l_prevLB1_State = (-1);	// force initial calling of LP2_SignalState()
    l_prevLB2_State = (-1);	// same for LB#2

    /* Setup PWM timer for the IR LED */
    PWM_TimerSetup();

    /* Initialize LETIMER0 */
    LETIMER0_setup();
}
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

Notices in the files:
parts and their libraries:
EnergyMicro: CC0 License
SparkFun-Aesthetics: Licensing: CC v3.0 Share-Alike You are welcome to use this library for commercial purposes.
